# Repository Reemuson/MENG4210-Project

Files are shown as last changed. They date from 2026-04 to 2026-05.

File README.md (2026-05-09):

<p align="center" width="100%">
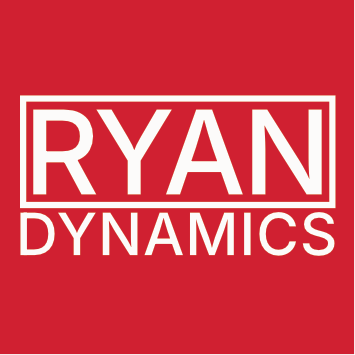
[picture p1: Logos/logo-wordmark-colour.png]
  
</p>

<h1 align="center">DREAM</h1>

<h2 align="center">Data Recording and Electrophysiological Acquisition Module</h2>

<p align="center" width="100%">
  <a href="https://github.com/Reemuson/MENG4210-Project/actions/workflows/ci.yaml">
    
  </a>
</p>

<p align="center" width="100%">
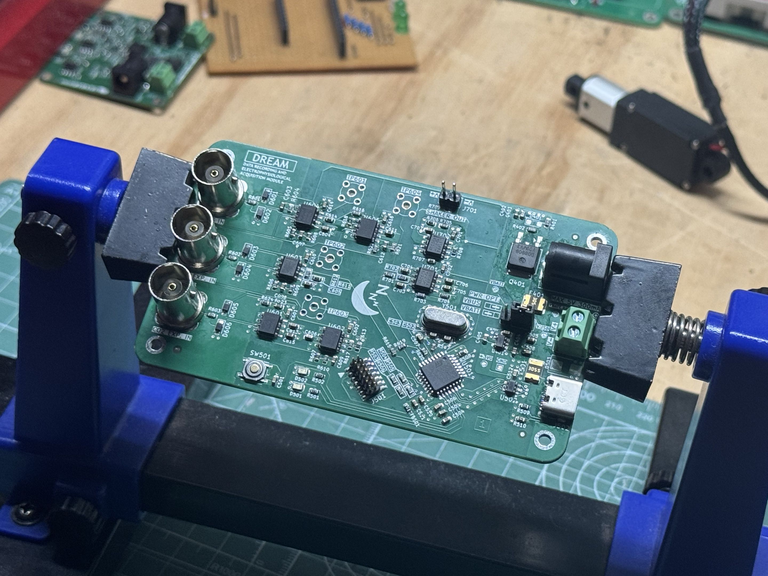
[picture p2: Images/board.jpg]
    
</p>

***

<p align="center">
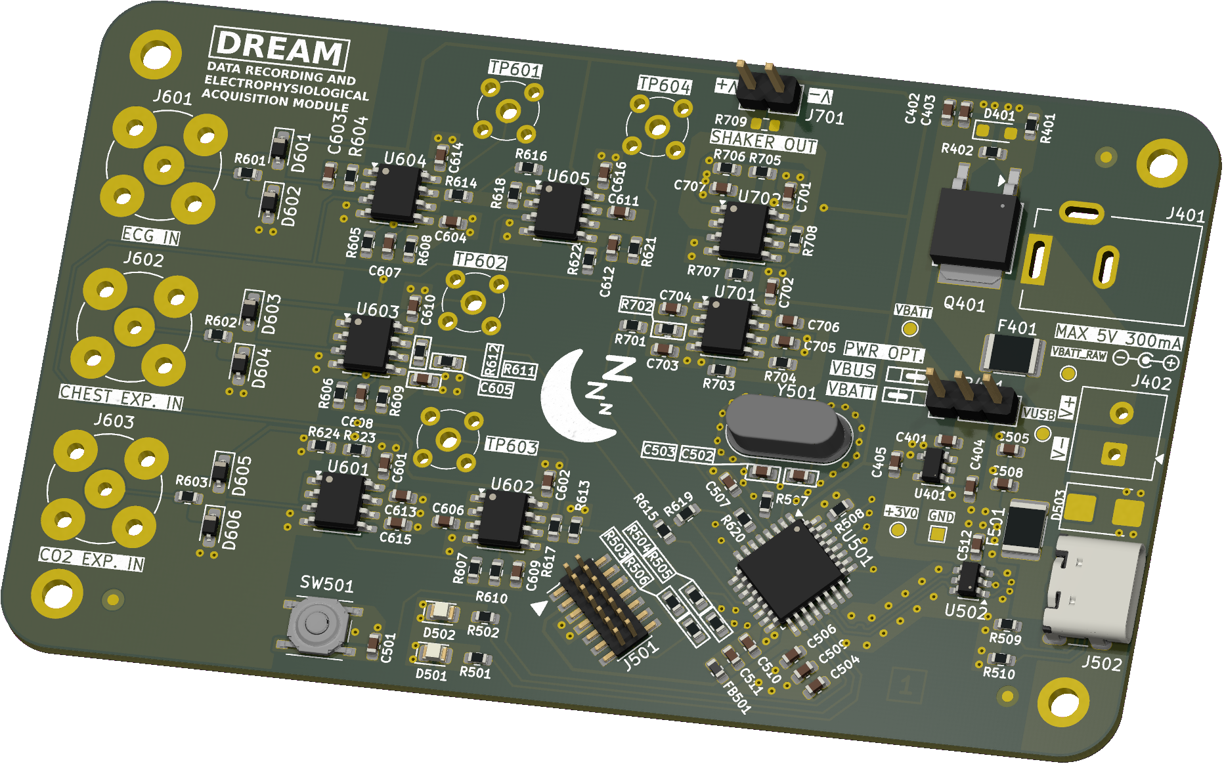
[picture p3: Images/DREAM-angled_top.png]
3D Top Angled
  
&nbsp; &nbsp; &nbsp; &nbsp;
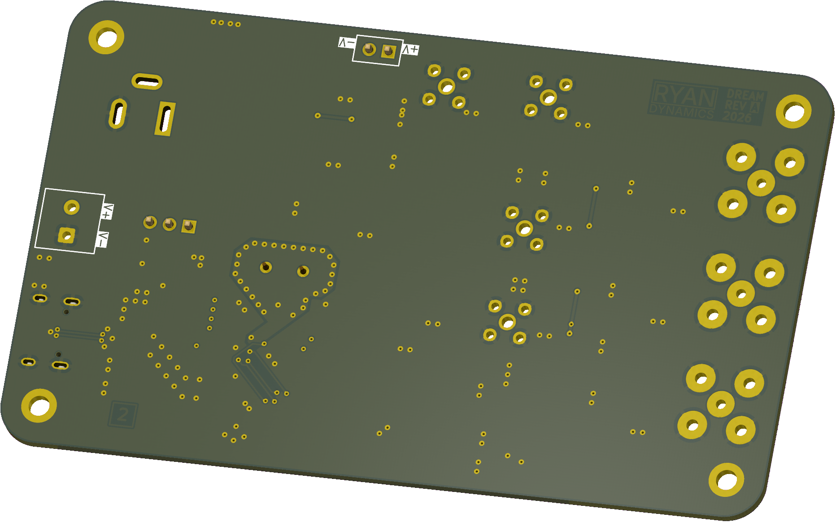
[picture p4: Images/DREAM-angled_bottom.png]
3D Bottom Angled
  
</p>

***

## SPECIFICATIONS

| Parameter | Value | 
| --- | --- |
| Dimensions | 100.0 × 60.0 mm |

***

## DIRECTORY STRUCTURE

    .
    ├─ Computations       # Misc calculations
    ├─ HTML               # HTML files for generated webpage
    ├─ Images             # Pictures and renders
    │
    ├─ kibot_resources    # External resources for KiBot
    │  ├─ colors          # Color theme for KiCad
    │  ├─ fonts           # Fonts used in the project
    │  ├─ scripts         # External scripts used with KiBot
    │  └─ templates       # Templates for KiBot generated reports
    │
    ├─ kibot_yaml         # KiBot YAML config files
    ├─ KiRI               # KiRI (PCB diff viewer) files
    │
    ├─ lib                # KiCad footprint and symbol libraries
    │  ├─ 3d_models       # Component 3D models
    │  ├─ lib_fp          # Footprint libraries
    │  └─ lib_sym         # Symbol libraries
    │
    ├─ Logos              # Logos
    │
    ├─ Manufacturing      # Assembly and fabrication documents
    │  ├─ Assembly        # Assembly documents (BoM, pos, notes)
    │  │
    │  └─ Fabrication     # Fabrication documents (ZIP, notes)
    │     ├─ Drill Tables # CSV drill tables
    │     └─ Gerbers      # Gerbers
    │
    ├─ Report             # Reports for ERC/DRC
    ├─ Schematic          # PDF of schematic
    ├─ Templates          # Title block templates
    ├─ Testing
    │  └─ Testpoints      # Testpoints tables      
    │
    └─ Variants           # Outputs for assembly variants

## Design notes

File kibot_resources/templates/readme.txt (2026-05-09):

<p align="center" width="100%">
  
</p>

<h1 align="center">${BOARD_NAME}</h1>

<h2 align="center">Data Recording and Electrophysiological Acquisition Module</h2>

<p align="center" width="100%">
  <a href="${GIT_URL}/actions/workflows/ci.yaml">
    CI Badge
  </a>
</p>

<p align="center" width="100%">
    
</p>

***

<p align="center">
  3D Top Angled
&nbsp; &nbsp; &nbsp; &nbsp;
  3D Bottom Angled
</p>

***

## SPECIFICATIONS

| Parameter | Value | 
| --- | --- |
| Dimensions | ${bb_w_mm} × ${bb_h_mm} mm |

***

## DIRECTORY STRUCTURE

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

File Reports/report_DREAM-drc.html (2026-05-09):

Logo

(https://github.com/INTI-CMNB/KiBot/) | DRC report for DREAM
| PCB: DREAM Revision: 1.2.0 Date: 2026-05-09T09:53:02+0000 KiCad Version: 9.0.7 | Errors: 2 Warnings: 344 Total: 346

Violations

Type | Description | Details
drill_out_of_range | Hole size out of range (rule 'MENG4210 Minimum Non-plated Hole Size' min hole 0.8000 mm; actual 0.6500 mm) | @(256.22 mm, 150.39 mm): NPTH pad of J502
drill_out_of_range | Hole size out of range (rule 'MENG4210 Minimum Non-plated Hole Size' min hole 0.8000 mm; actual 0.6500 mm) | @(256.22 mm, 144.61 mm): NPTH pad of J502
via_dangling | Via is not connected or connected on only one layer | @(237.43 mm, 143.45 mm): Via [unconnected-(U501-PB5-Pad28)] on L1 (Sig, PWR) - L2 (Sig, GND)
via_dangling | Via is not connected or connected on only one layer | @(237.43 mm, 142.18 mm): Via [unconnected-(U501-PB6-Pad29)] on L1 (Sig, PWR) - L2 (Sig, GND)
via_dangling | Via is not connected or connected on only one layer | @(237.43 mm, 140.91 mm): Via [unconnected-(U501-PB7-Pad30)] on L1 (Sig, PWR) - L2 (Sig, GND)
via_dangling | Via is not connected or connected on only one layer | @(238.7 mm, 147.26 mm): Via [unconnected-(U501-PA15-Pad25)] on L1 (Sig, PWR) - L2 (Sig, GND)
via_dangling | Via is not connected or connected on only one layer | @(237.43 mm, 144.72 mm): Via [unconnected-(U501-PB4-Pad27)] on L1 (Sig, PWR) - L2 (Sig, GND)
via_dangling | Via is not connected or connected on only one layer | @(224.879798 mm, 146.139798 mm): Via [unconnected-(U501-PA3-Pad8)] on L1 (Sig, PWR) - L2 (Sig, GND)
via_dangling | Via is not connected or connected on only one layer | @(224.095 mm, 144.72 mm): Via [unconnected-(U501-PA2-Pad7)] on L1 (Sig, PWR) - L2 (Sig, GND)
lib_footprint_mismatch | Footprint 'SOT-23-6' does not match copy in library 'Package_TO_SOT_SMD'. | @(247.5 mm, 147.5 mm): Footprint U502
lib_footprint_mismatch | Footprint 'R_0603_1608Metric' does not match copy in library 'Resistor_SMD'. | @(195.52 mm, 132.02 mm): Footprint R612
lib_footprint_mismatch | Footprint 'R_0603_1608Metric' does not match copy in library 'Resistor_SMD'. | @(192.98 mm, 122.685 mm): Footprint R608
lib_footprint_mismatch | Footprint 'D_SOD-323_HandSoldering' does not match copy in library 'Diode_SMD'. | @(180.0 mm, 150.0 mm): Footprint D606
lib_footprint_mismatch | Footprint 'R_0603_1608Metric' does not match copy in library 'Resistor_SMD'. | @(196.345 mm, 117.415 mm): Footprint R614
lib_footprint_mismatch | Footprint 'R_0603_1608Metric' does not match copy in library 'Resistor_SMD'. | @(208.855 mm, 122.05 mm): Footprint R622
lib_footprint_mismatch | Footprint 'R_0603_1608Metric' does not match copy in library 'Resistor_SMD'. | @(227.46 mm, 129.48 mm): Footprint R704
lib_footprint_mismatch | Footprint 'PinHeader_1x03_P2.54mm_Vertical' does not match copy in library 'Connector_PinHeader_2.54mm'. | @(242.46 mm, 131.5 mm): Footprint JP401
lib_footprint_mismatch | Footprint 'C_0603_1608Metric' does not match copy in library 'Capacitor_SMD'. | @(233.071992 mm, 156.063008 mm): Footprint C506
lib_footprint_mismatch | Footprint 'C_0603_1608Metric' does not match copy in library 'Capacitor_SMD'. | @(229.088008 mm, 155.428008 mm): Footprint C510
lib_footprint_mismatch | Footprint 'R_0603_1608Metric' does not match copy in library 'Resistor_SMD'. | @(198.06 mm, 132.655 mm): Footprint R611
lib_footprint_mismatch | Footprint 'R_0603_1608Metric' does not match copy in library 'Resistor_SMD'. | @(201.235 mm, 116.78 mm): Footprint R618
lib_footprint_mismatch | Footprint 'C_0603_1608Metric' does not match copy in library 'Capacitor_SMD'. | @(191.075 mm, 122.635 mm): Footprint C607
lib_footprint_mismatch | Footprint 'L_0603_1608Metric' does not match copy in library 'Inductor_SMD'. | @(226.635 mm, 158.055 mm): Footprint FB501
lib_footprint_mismatch | Footprint 'D_SOD-323_HandSoldering' does not match copy in library 'Diode_SMD'. | @(180.0 mm, 130.0 mm): Footprint D603
lib_footprint_mismatch | Footprint 'R_0603_1608Metric' does not match copy in library 'Resistor_SMD'. | @(221.4788 mm, 144.1612 mm): Footprint R619
lib_footprint_mismatch | Footprint 'D_SOD-323_HandSoldering' does not match copy in library 'Diode_SMD'. | @(180.0 mm, 135.0 mm): Footprint D604
lib_footprint_mismatch | Footprint 'R_0603_1608Metric' does not match copy in library 'Resistor_SMD'. | @(221.696698 mm, 152.356372 mm): Footprint R503
lib_footprint_mismatch | Footprint 'SOIC-8_3.9x4.9mm_P1.27mm' does not match copy in library 'Package_SO'. | @(191.075 mm, 146.625 mm): Footprint U601
lib_footprint_mismatch | Footprint 'C_0603_1608Metric' does not match copy in library 'Capacitor_SMD'. | @(196.155 mm, 159.185 mm): Footprint C501
lib_footprint_mismatch | Footprint 'R_0603_1608Metric' does not match copy in library 'Resistor_SMD'. | @(203.775 mm, 151.26 mm): Footprint R607
lib_footprint_mismatch | Footprint 'R_0603_1608Metric' does not match copy in library 'Resistor_SMD'. | @(210.125 mm, 146.625 mm): Footprint R617
lib_footprint_mismatch | Footprint 'R_0603_1608Metric' does not match copy in library 'Resistor_SMD'. | @(177.5 mm, 147.5 mm): Footprint R603
lib_footprint_mismatch | Footprint 'R_0603_1608Metric' does not match copy in library 'Resistor_SMD'. | @(186.63 mm, 116.78 mm): Footprint R604
lib_footprint_mismatch | Footprint 'R_0603_1608Metric' does not match copy in library 'Resistor_SMD'. | @(242.5 mm, 108.285499 mm): Footprint R402
lib_footprint_mismatch | Footprint 'C_0603_1608Metric' does not match copy in library 'Capacitor_SMD'. | @(224.816992 mm, 140.996992 mm): Footprint C507
lib_footprint_mismatch | Footprint 'D_SOD-323_HandSoldering' does not match copy in library 'Diode_SMD'. | @(180.0 mm, 145.0 mm): Footprint D605
lib_footprint_mismatch | Footprint 'R_1812_4532Metric' does not match copy in library 'Resistor_SMD'. | @(251.4 mm, 142.18 mm): Footprint F501
lib_footprint_mismatch | Footprint 'LQFP-32_7x7mm_P0.8mm' does not match copy in library 'Package_QFP'. | @(231.715 mm, 148.53 mm): Footprint U501
lib_footprint_mismatch | Footprint 'LED_0805_2012Metric' does not match copy in library 'LED_SMD'. | @(201.6668 mm, 159.325 mm): Footprint D501
lib_footprint_mismatch | Footprint 'R_0603_1608Metric' does not match copy in library 'Resistor_SMD'. | @(177.5 mm, 132.5 mm): Footprint R602
lib_footprint_mismatch | Footprint 'R_0603_1608Metric' does not match copy in library 'Resistor_SMD'. | @(226.635 mm, 118.05 mm): Footprint R708
lib_footprint_mismatch | Footprint 'PinHeader_1x02_P2.54mm_Vertical' does not match copy in library 'Connector_PinHeader_2.54mm'. | @(220.915 mm, 105.35 mm): Footprint J701
lib_footprint_mismatch | Footprint 'SOT-23-5' does not match copy in library 'Package_TO_SOT_SMD'. | @(242.5 mm, 137.5 mm): Footprint U401
lib_footprint_mismatch | Footprint 'R_0603_1608Metric' does not match copy in library 'Resistor_SMD'. | @(188.345 mm, 141.545 mm): Footprint R624
lib_footprint_mismatch | Footprint 'R_0603_1608Metric' does not match copy in library 'Resistor_SMD'. | @(191.52 mm, 141.545 mm): Footprint R623
lib_footprint_mismatch | Footprint 'C_0603_1608Metric' does not match copy in library 'Capacitor_SMD'. | @(184.725 mm, 116.78 mm): Footprint C603
lib_footprint_mismatch | Footprint 'R_0603_1608Metric' does not match copy in library 'Resistor_SMD'. | @(226.635 mm, 144.085 mm): Footprint R620
lib_footprint_mismatch | Footprint 'R_0603_1608Metric' does not match copy in library 'Resistor_SMD'. | @(219.775326 mm, 145.9138 mm): Footprint R615
lib_footprint_mismatch | Footprint 'SOIC-8_3.9x4.9mm_P1.27mm' does not match copy in library 'Package_SO'. | @(222.19 mm, 126.94 mm): Footprint U701
lib_footprint_mismatch | Footprint 'R_0603_1608Metric' does not match copy in library 'Resistor_SMD'. | @(245.5 mm, 105.460499 mm): Footprint R401
lib_footprint_mismatch | Footprint 'R_0603_1608Metric' does not match copy in library 'Resistor_SMD'. | @(222.19 mm, 130.75 mm): Footprint R703
lib_footprint_mismatch | Footprint 'C_0603_1608Metric' does not match copy in library 'Capacitor_SMD'. | @(194.25 mm, 142.675 mm): Footprint C601
lib_footprint_mismatch | Footprint 'R_0603_1608Metric' does not match copy in library 'Resistor_SMD'. | @(202.06 mm, 114.24 mm): Footprint R616
lib_footprint_mismatch | Footprint 'C_0603_1608Metric' does not match copy in library 'Capacitor_SMD'. | @(208.855 mm, 114.1 mm): Footprint C616
lib_footprint_mismatch | Footprint 'R_0603_1608Metric' does not match copy in library 'Resistor_SMD'. | @(189.17 mm, 136.655 mm): Footprint R606
lib_footprint_mismatch | Footprint 'R_0603_1608Metric' does not match copy in library 'Resistor_SMD'. | @(205.68 mm, 151.26 mm): Footprint R610
lib_footprint_mismatch | Footprint 'R_0603_1608Metric' does not match copy in library 'Resistor_SMD'. | @(251.4 mm, 154.245 mm): Footprint R510
lib_footprint_mismatch | Footprint 'R_0603_1608Metric' does not match copy in library 'Resistor_SMD'. | @(177.5 mm, 117.5 mm): Footprint R601
lib_footprint_mismatch | Footprint 'C_0603_1608Metric' does not match copy in library 'Capacitor_SMD'. | @(196.295 mm, 145.355 mm): Footprint C613
lib_footprint_mismatch | Footprint 'C_0603_1608Metric' does not match copy in library 'Capacitor_SMD'. | @(235.611992 mm, 158.603008 mm): Footprint C504
lib_footprint_mismatch | Footprint 'D_SOD-323_HandSoldering' does not match copy in library 'Diode_SMD'. | @(180.0 mm, 115.0 mm): Footprint D601
lib_footprint_mismatch | Footprint 'R_0603_1608Metric' does not match copy in library 'Resistor_SMD'. | @(211.9284 mm, 146.625 mm): Footprint R613
lib_footprint_mismatch | Footprint 'C_0603_1608Metric' does not match copy in library 'Capacitor_SMD'. | @(200.46 mm, 147.26 mm): Footprint C606
lib_footprint_mismatch | Footprint 'D_SOD-323_HandSoldering' does not match copy in library 'Diode_SMD'. | @(180.0 mm, 120.0 mm): Footprint D602
lib_footprint_mismatch | Footprint 'SOIC-8_3.9x4.9mm_P1.27mm' does not match copy in library 'Package_SO'. | @(205.68 mm, 146.625 mm): Footprint U602
lib_footprint_mismatch | Footprint 'C_0603_1608Metric' does not match copy in library 'Capacitor_SMD'. | @(239.0 mm, 137.499999 mm): Footprint C405
lib_footprint_mismatch | Footprint 'C_0603_1608Metric' does not match copy in library 'Capacitor_SMD'. | @(227.41 mm, 127.575 mm): Footprint C705
lib_footprint_mismatch | Footprint 'LED_0805_2012Metric' does not match copy in library 'LED_SMD'. | @(201.6668 mm, 155.515 mm): Footprint D502
lib_footprint_mismatch | Footprint 'C_0603_1608Metric' does not match copy in library 'Capacitor_SMD'. | @(234.341992 mm, 157.333008 mm): Footprint C509
lib_footprint_mismatch | Footprint 'R_0603_1608Metric' does not match copy in library 'Resistor_SMD'. | @(213.745 mm, 127.575 mm): Footprint R701
lib_footprint_mismatch | Footprint 'R_0603_1608Metric' does not match copy in library 'Resistor_SMD'. | @(205.4768 mm, 159.325 mm): Footprint R501
lib_footprint_mismatch | Footprint 'C_0603_1608Metric' does not match copy in library 'Capacitor_SMD'. | @(227.41 mm, 125.67 mm): Footprint C706
lib_footprint_mismatch | Footprint 'C_0603_1608Metric' does not match copy in library 'Capacitor_SMD'. | @(194.25 mm, 128.07 mm): Footprint C610
lib_footprint_mismatch | Footprint 'C_0603_1608Metric' does not match copy in library 'Capacitor_SMD'. | @(191.075 mm, 136.605 mm): Footprint C608
lib_footprint_mismatch | Footprint 'R_0603_1608Metric' does not match copy in library 'Resistor_SMD'. | @(234.838363 mm, 142.231637 mm): Footprint R508
lib_footprint_mismatch | Footprint 'C_0603_1608Metric' does not match copy in library 'Capacitor_SMD'. | @(248.86 mm, 135.195 mm): Footprint C505
lib_footprint_mismatch | Footprint 'R_0603_1608Metric' does not match copy in library 'Resistor_SMD'. | @(228.286 mm, 142.434 mm): Footprint R507
lib_footprint_mismatch | Footprint 'R_1812_4532Metric' does not match copy in library 'Resistor_SMD'. | @(247.5 mm, 126.5 mm): Footprint F401
lib_footprint_mismatch | Footprint 'TerminalBlock_Phoenix_MKDS-1-2-3.81_1x02_P3.81mm_Horizontal' does not match copy in library 'TerminalBlock_Phoenix'. | @(257.972301 mm, 134.433001 mm): Footprint J402
lib_footprint_mismatch | Footprint 'BarrelJack_Kycon_KLDX-0202-xC_Horizontal' does not match copy in library 'Connector_BarrelJack'. | @(248.05 mm, 117.5 mm): Footprint J401
lib_footprint_mismatch | Footprint 'SOIC-8_3.9x4.9mm_P1.27mm' does not match copy in library 'Package_SO'. | @(191.075 mm, 118.05 mm): Footprint U604
lib_footprint_mismatch | Footprint 'R_0603_1608Metric' does not match copy in library 'Resistor_SMD'. | @(216.92 mm, 127.575 mm): Footprint R702
lib_footprint_mismatch | Footprint 'SOIC-8_3.9x4.9mm_P1.27mm' does not match copy in library 'Package_SO'. | @(191.075 mm, 132.02 mm): Footprint U603
lib_footprint_mismatch | Footprint 'C_0603_1608Metric' does not match copy in library 'Capacitor_SMD'. | @(219.46 mm, 114.24 mm): Footprint C707
lib_footprint_mismatch | Footprint 'R_0603_1608Metric' does not match copy in library 'Resistor_SMD'. | @(223.941762 mm, 154.601438 mm): Footprint R506
lib_footprint_mismatch | Footprint 'R_0603_1608Metric' does not match copy in library 'Resistor_SMD'. | @(251.4 mm, 151.07 mm): Footprint R509
lib_footprint_mismatch | Footprint 'C_0603_1608Metric' does not match copy in library 'Capacitor_SMD'. | @(243.275 mm, 135.0 mm): Footprint C401
lib_footprint_mismatch | Footprint 'C_0603_1608Metric' does not match copy in library 'Capacitor_SMD'. | @(248.86 mm, 138.37 mm): Footprint C508
lib_footprint_mismatch | Footprint 'R_0603_1608Metric' does not match copy in library 'Resistor_SMD'. | @(212.665 mm, 120.59 mm): Footprint R621
lib_footprint_mismatch | Footprint 'C_0603_1608Metric' does not match copy in library 'Capacitor_SMD'. | @(194.25 mm, 114.1 mm): Footprint C614
lib_footprint_mismatch | Footprint 'R_0603_1608Metric' does not match copy in library 'Resistor_SMD'. | @(225.872163 mm, 153.837763 mm): Footprint R505
lib_footprint_mismatch | Footprint 'C_0603_1608Metric' does not match copy in library 'Capacitor_SMD'. | @(216.92 mm, 129.48 mm): Footprint C703
lib_footprint_mismatch | Footprint 'C_0603_1608Metric' does not match copy in library 'Capacitor_SMD'. | @(225.365 mm, 122.99 mm): Footprint C702
lib_footprint_mismatch | Footprint 'C_0603_1608Metric' does not match copy in library 'Capacitor_SMD'. | @(196.295 mm, 134.56 mm): Footprint C605
lib_footprint_mismatch | Footprint 'C_0603_1608Metric' does not match copy in library 'Capacitor_SMD'. | @(238.0 mm, 105.0 mm): Footprint C402
lib_footprint_mismatch | Footprint 'C_0603_1608Metric' does not match copy in library 'Capacitor_SMD'. | @(210.76 mm, 120.59 mm): Footprint C612
lib_footprint_mismatch | Footprint 'C_0603_1608Metric' does not match copy in library 'Capacitor_SMD'. | @(247.5 mm, 144.225 mm): Footprint C512
lib_footprint_mismatch | Footprint 'C_0603_1608Metric' does not match copy in library 'Capacitor_SMD'. | @(225.365 mm, 114.1 mm): Footprint C701
lib_footprint_mismatch | Footprint 'R_0603_1608Metric' does not match copy in library 'Resistor_SMD'. | @(222.0884 mm, 107.89 mm): Footprint R709
lib_footprint_mismatch | Footprint 'C_0603_1608Metric' does not match copy in library 'Capacitor_SMD'. | @(196.295 mm, 119.955 mm): Footprint C604
lib_footprint_mismatch | Footprint 'C_0603_1608Metric' does not match copy in library 'Capacitor_SMD'. | @(230.840001 mm, 139.64 mm): Footprint C502
lib_footprint_mismatch | Footprint 'SOIC-8_3.9x4.9mm_P1.27mm' does not match copy in library 'Package_SO'. | @(222.19 mm, 118.05 mm): Footprint U702
lib_footprint_mismatch | Footprint 'C_0603_1608Metric' does not match copy in library 'Capacitor_SMD'. | @(207.585 mm, 151.21 mm): Footprint C609
lib_footprint_mismatch | Footprint 'R_0603_1608Metric' does not match copy in library 'Resistor_SMD'. | @(219.46 mm, 112.335 mm): Footprint R706
lib_footprint_mismatch | Footprint 'C_0603_1608Metric' does not match copy in library 'Capacitor_SMD'. | @(246.0 mm, 139.025 mm): Footprint C404
lib_footprint_mismatch | Footprint 'R_0603_1608Metric' does not match copy in library 'Resistor_SMD'. | @(205.4768 mm, 155.515 mm): Footprint R502
lib_footprint_mismatch | Footprint 'C_0603_1608Metric' does not match copy in library 'Capacitor_SMD'. | @(216.97 mm, 125.67 mm): Footprint C704
lib_footprint_mismatch | Footprint 'SOIC-8_3.9x4.9mm_P1.27mm' does not match copy in library 'Package_SO'. | @(205.68 mm, 118.05 mm): Footprint U605
lib_footprint_mismatch | Footprint 'C_0603_1608Metric' does not match copy in library 'Capacitor_SMD'. | @(239.5 mm, 105.0 mm): Footprint C403
lib_footprint_mismatch | Footprint 'R_0603_1608Metric' does not match copy in library 'Resistor_SMD'. | @(192.98 mm, 136.655 mm): Footprint R609
lib_footprint_mismatch | Footprint 'PinHeader_2x07_P1.27mm_Vertical_SMD' does not match copy in library 'Connector_PinHeader_1.27mm'. | @(215.84 mm, 153.61 mm): Footprint J501
lib_footprint_mismatch | Footprint 'C_0603_1608Metric' does not match copy in library 'Capacitor_SMD'. | @(227.818008 mm, 156.698008 mm): Footprint C511
lib_footprint_mismatch | Footprint 'R_0603_1608Metric' does not match copy in library 'Resistor_SMD'. | @(189.17 mm, 122.685 mm): Footprint R605
lib_footprint_mismatch | Footprint 'C_0603_1608Metric' does not match copy in library 'Capacitor_SMD'. | @(210.9 mm, 117.415 mm): Footprint C611
lib_footprint_mismatch | Footprint 'R_0603_1608Metric' does not match copy in library 'Resistor_SMD'. | @(222.635 mm, 112.335 mm): Footprint R705
lib_footprint_mismatch | Footprint 'C_0603_1608Metric' does not match copy in library 'Capacitor_SMD'. | @(208.855 mm, 142.675 mm): Footprint C602
lib_footprint_mismatch | Footprint 'C_0603_1608Metric' does not match copy in library 'Capacitor_SMD'. | @(227.511 mm, 139.64 mm): Footprint C503
lib_footprint_mismatch | Footprint 'R_0603_1608Metric' does not match copy in library 'Resistor_SMD'. | @(223.627099 mm, 151.592697 mm): Footprint R504
lib_footprint_mismatch | Footprint 'R_0603_1608Metric' does not match copy in library 'Resistor_SMD'. | @(222.19 mm, 121.86 mm): Footprint R707
lib_footprint_mismatch | Footprint 'C_0603_1608Metric' does not match copy in library 'Capacitor_SMD'. | @(196.295 mm, 147.895 mm): Footprint C615
silk_over_copper | Silkscreen clipped by solder mask | @(194.8088 mm, 133.8488 mm): Rectangle on F.Silkscreen
silk_over_copper | Silkscreen clipped by solder mask | @(226.0 mm, 138.9288 mm): Rectangle on F.Silkscreen
silk_over_copper | Silkscreen clipped by solder mask | @(229.4036 mm, 138.9288 mm): Rectangle on F.Silkscreen
silk_over_copper | Silkscreen clipped by solder mask | @(247.5 mm, 150.25 mm): Reference field of U502
silk_over_copper | Silkscreen clipped by solder mask | @(231.1816 mm, 157.4708 mm): Reference field of C510
silk_over_copper | Silkscreen clipped by solder mask | @(191.075 mm, 125.035 mm): Reference field of C607
silk_over_copper | Silkscreen clipped by solder mask | @(248.75 mm, 142.18 mm): Reference field of F501
silk_over_copper | Silkscreen clipped by solder mask | @(236.9728 mm, 145.532801 mm): Reference field of U501
silk_over_copper | Silkscreen clipped by solder mask | @(199.9818 mm, 158.365 mm): Segment of D501 on F.Silkscreen
silk_over_copper | Silkscreen clipped by solder mask | @(199.9818 mm, 160.285 mm): Segment of D501 on F.Silkscreen
silk_over_copper | Silkscreen clipped by solder mask | @(202.6668 mm, 158.365 mm): Segment of D501 on F.Silkscreen
silk_over_copper | Silkscreen clipped by solder mask | @(191.52 mm, 140.275 mm): Reference field of R623
silk_over_copper | Silkscreen clipped by solder mask | @(254.335001 mm, 137.49 mm): Segment of D503 on F.Silkscreen
silk_over_copper | Silkscreen clipped by solder mask | @(254.335001 mm, 141.79 mm): Segment of D503 on F.Silkscreen
silk_over_copper | Silkscreen clipped by solder mask | @(212.03 mm, 143.45 mm): Reference field of R613
silk_over_copper | Silkscreen clipped by solder mask | @(230.445 mm, 127.575 mm): Reference field of C705
silk_over_copper | Silkscreen clipped by solder mask | @(199.9818 mm, 154.555 mm): Segment of D502 on F.Silkscreen
silk_over_copper | Silkscreen clipped by solder mask | @(199.9818 mm, 156.475 mm): Segment of D502 on F.Silkscreen
silk_over_copper | Silkscreen clipped by solder mask | @(202.6668 mm, 154.555 mm): Segment of D502 on F.Silkscreen
silk_over_copper | Silkscreen clipped by solder mask | @(236.5156 mm, 155.184801 mm): Reference field of C509
silk_over_copper | Silkscreen clipped by solder mask | @(191.075 mm, 139.005 mm): Reference field of C608
silk_over_copper | Silkscreen clipped by solder mask | @(248.86 mm, 133.925 mm): Reference field of C505
silk_over_copper | Silkscreen clipped by solder mask | @(230.445 mm, 141.799 mm): Reference field of R507
silk_over_copper | Silkscreen clipped by solder mask | @(193.135 mm, 120.61 mm): Segment of U604 on F.Silkscreen
silk_over_copper | Silkscreen clipped by solder mask | @(193.135 mm, 134.58 mm): Segment of U603 on F.Silkscreen
silk_over_copper | Silkscreen clipped by solder mask | @(216.475 mm, 114.24 mm): Reference field of C707
silk_over_copper | Silkscreen clipped by solder mask | @(239.97 mm, 135.0 mm): Reference field of C401
silk_over_copper | Silkscreen clipped by solder mask | @(248.86 mm, 137.1 mm): Reference field of C508
silk_over_copper | Silkscreen clipped by solder mask | @(222.7488 mm, 114.6464 mm): Reference field of U702
silk_over_copper | Silkscreen clipped by solder mask | @(229.81 mm, 158.69 mm): Reference field of C511
nonmirrored_text_on_back_layer | Non-Mirrored text on back layer | @(225.238 mm, 104.7404 mm): PCB text 'V-' on B.Silkscreen
nonmirrored_text_on_back_layer | Non-Mirrored text on back layer | @(219.2436 mm, 104.7404 mm): PCB text 'V+' on B.Silkscreen

Schematic parity

Type | Description | Details
net_conflict | Pad net (/ARCHITECTURE/DIGITAL AND HMI/BTN) doesn't match net given by schematic (/CIRCUIT/BTN). | @(196.155 mm, 159.96 mm): Pad 2 [/ARCHITECTURE/DIGITAL AND HMI/BTN] of C501 on L1 (Sig, PWR)
net_conflict | Pad net (/ARCHITECTURE/DIGITAL AND HMI/OSC_IN) doesn't match net given by schematic (/CIRCUIT/OSC_IN). | @(231.615001 mm, 139.64 mm): Pad 2 [/ARCHITECTURE/DIGITAL AND HMI/OSC_IN] of C502 on L1 (Sig, PWR)
net_conflict | Pad net (/ARCHITECTURE/DIGITAL AND HMI/XTAL) doesn't match net given by schematic (/CIRCUIT/XTAL). | @(226.736 mm, 139.64 mm): Pad 1 [/ARCHITECTURE/DIGITAL AND HMI/XTAL] of C503 on L1 (Sig, PWR)
net_conflict | Pad net (/ARCHITECTURE/DIGITAL AND HMI/~{RST}) doesn't match net given by schematic (/CIRCUIT/~{RST}). | @(225.365 mm, 141.545 mm): Pad 2 [/ARCHITECTURE/DIGITAL AND HMI/~{RST}] of C507 on L1 (Sig, PWR)
net_conflict | Pad net (/ARCHITECTURE/DIGITAL AND HMI/VDDA) doesn't match net given by schematic (VDDA). | @(228.54 mm, 154.88 mm): Pad 2 [/ARCHITECTURE/DIGITAL AND HMI/VDDA] of C510 on L1 (Sig, PWR)
net_conflict | Pad net (/ARCHITECTURE/DIGITAL AND HMI/VDDA) doesn't match net given by schematic (VDDA). | @(227.27 mm, 156.15 mm): Pad 2 [/ARCHITECTURE/DIGITAL AND HMI/VDDA] of C511 on L1 (Sig, PWR)
net_conflict | Pad net (/ARCHITECTURE/ANALOGUE INPUTS/ECG_LPF1) doesn't match net given by schematic (/CIRCUIT/ECG_LPF1). | @(184.725 mm, 116.005 mm): Pad 1 [/ARCHITECTURE/ANALOGUE INPUTS/ECG_LPF1] of C603 on L1 (Sig, PWR)
net_conflict | Pad net (/ARCHITECTURE/ANALOGUE INPUTS/ECG_LPF1_N) doesn't match net given by schematic (/CIRCUIT/ECG_LPF1_N). | @(184.725 mm, 117.555 mm): Pad 2 [/ARCHITECTURE/ANALOGUE INPUTS/ECG_LPF1_N] of C603 on L1 (Sig, PWR)
net_conflict | Pad net (/ARCHITECTURE/ANALOGUE INPUTS/ECG_SK_RC) doesn't match net given by schematic (/CIRCUIT/ECG_SK_RC). | @(195.52 mm, 119.955 mm): Pad 1 [/ARCHITECTURE/ANALOGUE INPUTS/ECG_SK_RC] of C604 on L1 (Sig, PWR)
net_conflict | Pad net (/ARCHITECTURE/ANALOGUE INPUTS/CE_SK_RC) doesn't match net given by schematic (/CIRCUIT/CE_SK_RC). | @(195.52 mm, 134.56 mm): Pad 1 [/ARCHITECTURE/ANALOGUE INPUTS/CE_SK_RC] of C605 on L1 (Sig, PWR)
net_conflict | Pad net (/ARCHITECTURE/ANALOGUE INPUTS/CO2_SK_RC) doesn't match net given by schematic (/CIRCUIT/CO2_SK_RC). | @(201.235 mm, 147.26 mm): Pad 1 [/ARCHITECTURE/ANALOGUE INPUTS/CO2_SK_RC] of C606 on L1 (Sig, PWR)
net_conflict | Pad net (/ARCHITECTURE/ANALOGUE INPUTS/ECG_FILT) doesn't match net given by schematic (/CIRCUIT/ECG_FILT). | @(191.075 mm, 121.86 mm): Pad 1 [/ARCHITECTURE/ANALOGUE INPUTS/ECG_FILT] of C607 on L1 (Sig, PWR)
net_conflict | Pad net (/ARCHITECTURE/ANALOGUE INPUTS/ECG_SK_MID) doesn't match net given by schematic (/CIRCUIT/ECG_SK_MID). | @(191.075 mm, 123.41 mm): Pad 2 [/ARCHITECTURE/ANALOGUE INPUTS/ECG_SK_MID] of C607 on L1 (Sig, PWR)
net_conflict | Pad net (/ARCHITECTURE/ANALOGUE INPUTS/CE_FILT) doesn't match net given by schematic (/CIRCUIT/CE_FILT). | @(191.075 mm, 135.83 mm): Pad 1 [/ARCHITECTURE/ANALOGUE INPUTS/CE_FILT] of C608 on L1 (Sig, PWR)
net_conflict | Pad net (/ARCHITECTURE/ANALOGUE INPUTS/CE_SK_MID) doesn't match net given by schematic (/CIRCUIT/CE_SK_MID). | @(191.075 mm, 137.38 mm): Pad 2 [/ARCHITECTURE/ANALOGUE INPUTS/CE_SK_MID] of C608 on L1 (Sig, PWR)
net_conflict | Pad net (/ARCHITECTURE/ANALOGUE INPUTS/CO2_FILT) doesn't match net given by schematic (/CIRCUIT/CO2_FILT). | @(207.585 mm, 150.435 mm): Pad 1 [/ARCHITECTURE/ANALOGUE INPUTS/CO2_FILT] of C609 on L1 (Sig, PWR)
net_conflict | Pad net (/ARCHITECTURE/ANALOGUE INPUTS/CO2_SK_MID) doesn't match net given by schematic (/CIRCUIT/CO2_SK_MID). | @(207.585 mm, 151.985 mm): Pad 2 [/ARCHITECTURE/ANALOGUE INPUTS/CO2_SK_MID] of C609 on L1 (Sig, PWR)
net_conflict | Pad net (/ARCHITECTURE/ANALOGUE INPUTS/SERVO_N) doesn't match net given by schematic (/CIRCUIT/SERVO_N). | @(211.675 mm, 117.415 mm): Pad 1 [/ARCHITECTURE/ANALOGUE INPUTS/SERVO_N] of C611 on L1 (Sig, PWR)
net_conflict | Pad net (/ARCHITECTURE/ANALOGUE INPUTS/SERVO_OUT) doesn't match net given by schematic (/CIRCUIT/SERVO_OUT). | @(210.125 mm, 117.415 mm): Pad 2 [/ARCHITECTURE/ANALOGUE INPUTS/SERVO_OUT] of C611 on L1 (Sig, PWR)
net_conflict | Pad net (/ARCHITECTURE/ANALOGUE INPUTS/SERVO_P) doesn't match net given by schematic (/CIRCUIT/SERVO_P). | @(210.76 mm, 119.815 mm): Pad 2 [/ARCHITECTURE/ANALOGUE INPUTS/SERVO_P] of C612 on L1 (Sig, PWR)
net_conflict | Pad net (/ARCHITECTURE/ANALOGUE OUTPUTS/SHK_SK1_RC) doesn't match net given by schematic (/CIRCUIT/SHK_SK1_RC). | @(216.145 mm, 129.48 mm): Pad 1 [/ARCHITECTURE/ANALOGUE OUTPUTS/SHK_SK1_RC] of C703 on L1 (Sig, PWR)
net_conflict | Pad net (/ARCHITECTURE/ANALOGUE OUTPUTS/SHK_FILT1) doesn't match net given by schematic (/CIRCUIT/SHK_FILT1). | @(217.745 mm, 125.67 mm): Pad 1 [/ARCHITECTURE/ANALOGUE OUTPUTS/SHK_FILT1] of C704 on L1 (Sig, PWR)
net_conflict | Pad net (/ARCHITECTURE/ANALOGUE OUTPUTS/SHK_SK1_MID) doesn't match net given by schematic (/CIRCUIT/SHK_SK1_MID). | @(216.195 mm, 125.67 mm): Pad 2 [/ARCHITECTURE/ANALOGUE OUTPUTS/SHK_SK1_MID] of C704 on L1 (Sig, PWR)
net_conflict | Pad net (/ARCHITECTURE/ANALOGUE OUTPUTS/SHK_SK2_RC) doesn't match net given by schematic (/CIRCUIT/SHK_SK2_RC). | @(226.635 mm, 127.575 mm): Pad 1 [/ARCHITECTURE/ANALOGUE OUTPUTS/SHK_SK2_RC] of C705 on L1 (Sig, PWR)
net_conflict | Pad net (/ARCHITECTURE/ANALOGUE OUTPUTS/SHK_FILT2) doesn't match net given by schematic (/CIRCUIT/SHK_FILT2). | @(226.635 mm, 125.67 mm): Pad 1 [/ARCHITECTURE/ANALOGUE OUTPUTS/SHK_FILT2] of C706 on L1 (Sig, PWR)
net_conflict | Pad net (/ARCHITECTURE/ANALOGUE OUTPUTS/SHK_SK2_MID) doesn't match net given by schematic (/CIRCUIT/SHK_SK2_MID). | @(228.185 mm, 125.67 mm): Pad 2 [/ARCHITECTURE/ANALOGUE OUTPUTS/SHK_SK2_MID] of C706 on L1 (Sig, PWR)
net_conflict | Pad net (/ARCHITECTURE/ANALOGUE OUTPUTS/VREF_SHK) doesn't match net given by schematic (/CIRCUIT/VREF_SHK). | @(220.235 mm, 114.24 mm): Pad 1 [/ARCHITECTURE/ANALOGUE OUTPUTS/VREF_SHK] of C707 on L1 (Sig, PWR)
net_conflict | Pad net (/ARCHITECTURE/POWER/GATE_RPP) doesn't match net given by schematic (/CIRCUIT/GATE_RPP). | @(243.75 mm, 106.285499 mm): Pad 2 [/ARCHITECTURE/POWER/GATE_RPP] of D401 on L1 (Sig, PWR)
net_conflict | Pad net (/ARCHITECTURE/ANALOGUE INPUTS/ECG_LPF1_N) doesn't match net given by schematic (/CIRCUIT/ECG_LPF1_N). | @(180.0 mm, 116.249999 mm): Pad 2 [/ARCHITECTURE/ANALOGUE INPUTS/ECG_LPF1_N] of D601 on L1 (Sig, PWR)
net_conflict | Pad net (/ARCHITECTURE/ANALOGUE INPUTS/ECG_LPF1_N) doesn't match net given by schematic (/CIRCUIT/ECG_LPF1_N). | @(180.0 mm, 118.750001 mm): Pad 1 [/ARCHITECTURE/ANALOGUE INPUTS/ECG_LPF1_N] of D602 on L1 (Sig, PWR)
net_conflict | Pad net (/ARCHITECTURE/ANALOGUE INPUTS/CE_BUFF_IN) doesn't match net given by schematic (/CIRCUIT/CE_BUFF_IN). | @(180.0 mm, 131.249999 mm): Pad 2 [/ARCHITECTURE/ANALOGUE INPUTS/CE_BUFF_IN] of D603 on L1 (Sig, PWR)
net_conflict | Pad net (/ARCHITECTURE/ANALOGUE INPUTS/CE_BUFF_IN) doesn't match net given by schematic (/CIRCUIT/CE_BUFF_IN). | @(180.0 mm, 133.750001 mm): Pad 1 [/ARCHITECTURE/ANALOGUE INPUTS/CE_BUFF_IN] of D604 on L1 (Sig, PWR)
net_conflict | Pad net (/ARCHITECTURE/ANALOGUE INPUTS/CO2_BUFF_IN) doesn't match net given by schematic (/CIRCUIT/CO2_BUFF_IN). | @(180.0 mm, 146.249999 mm): Pad 2 [/ARCHITECTURE/ANALOGUE INPUTS/CO2_BUFF_IN] of D605 on L1 (Sig, PWR)
net_conflict | Pad net (/ARCHITECTURE/ANALOGUE INPUTS/CO2_BUFF_IN) doesn't match net given by schematic (/CIRCUIT/CO2_BUFF_IN). | @(180.0 mm, 148.750001 mm): Pad 1 [/ARCHITECTURE/ANALOGUE INPUTS/CO2_BUFF_IN] of D606 on L1 (Sig, PWR)
net_conflict | Pad net (/ARCHITECTURE/POWER/VBATT_RAW) doesn't match net given by schematic (/CIRCUIT/VBATT_RAW). | @(249.6375 mm, 126.5 mm): Pad 1 [/ARCHITECTURE/POWER/VBATT_RAW] of F401 on L1 (Sig, PWR)
net_conflict | Pad net (/ARCHITECTURE/POWER/VBATT_FUSED) doesn't match net given by schematic (/CIRCUIT/VBATT_FUSED). | @(245.3625 mm, 126.5 mm): Pad 2 [/ARCHITECTURE/POWER/VBATT_FUSED] of F401 on L1 (Sig, PWR)
net_conflict | Pad net (/ARCHITECTURE/DIGITAL AND HMI/VBUS) doesn't match net given by schematic (/CIRCUIT/VBUS). | @(251.4 mm, 144.3175 mm): Pad 1 [/ARCHITECTURE/DIGITAL AND HMI/VBUS] of F501 on L1 (Sig, PWR)
net_conflict | Pad net (/ARCHITECTURE/DIGITAL AND HMI/VDDA) doesn't match net given by schematic (VDDA). | @(226.078153 mm, 157.498153 mm): Pad 1 [/ARCHITECTURE/DIGITAL AND HMI/VDDA] of FB501 on L1 (Sig, PWR)
net_conflict | Pad net (/ARCHITECTURE/POWER/VBATT_RAW) doesn't match net given by schematic (/CIRCUIT/VBATT_RAW). | @(248.05 mm, 117.5 mm): PTH pad 1 [/ARCHITECTURE/POWER/VBATT_RAW] of J401
net_conflict | Pad net (/ARCHITECTURE/POWER/VBATT_RAW) doesn't match net given by schematic (/CIRCUIT/VBATT_RAW). | @(257.972301 mm, 130.623001 mm): PTH pad 2 [/ARCHITECTURE/POWER/VBATT_RAW] of J402
footprint_symbol_mismatch | Value (J501) doesn't match symbol value (Conn_ST_STDC14). | @(215.84 mm, 153.61 mm): Footprint J501
net_conflict | Pad net (/ARCHITECTURE/DIGITAL AND HMI/VBUS) doesn't match net given by schematic (/CIRCUIT/VBUS). | @(255.145 mm, 149.9 mm): Pad A4 [/ARCHITECTURE/DIGITAL AND HMI/VBUS] of J502 on L1 (Sig, PWR)
net_conflict | Pad net (/ARCHITECTURE/DIGITAL AND HMI/CC1) doesn't match net given by schematic (/CIRCUIT/CC1). | @(255.145001 mm, 148.75 mm): Pad A5 [/ARCHITECTURE/DIGITAL AND HMI/CC1] of J502 on L1 (Sig, PWR)
net_conflict | Pad net (/ARCHITECTURE/DIGITAL AND HMI/D+) doesn't match net given by schematic (/CIRCUIT/D+). | @(255.145 mm, 147.75 mm): Pad A6 [/ARCHITECTURE/DIGITAL AND HMI/D+] of J502 on L1 (Sig, PWR)
net_conflict | Pad net (/ARCHITECTURE/DIGITAL AND HMI/D-) doesn't match net given by schematic (/CIRCUIT/D-). | @(255.145 mm, 147.25 mm): Pad A7 [/ARCHITECTURE/DIGITAL AND HMI/D-] of J502 on L1 (Sig, PWR)
net_conflict | Pad net (/ARCHITECTURE/DIGITAL AND HMI/VBUS) doesn't match net given by schematic (/CIRCUIT/VBUS). | @(255.145 mm, 145.1 mm): Pad A9 [/ARCHITECTURE/DIGITAL AND HMI/VBUS] of J502 on L1 (Sig, PWR)
net_conflict | Pad net (/ARCHITECTURE/DIGITAL AND HMI/VBUS) doesn't match net given by schematic (/CIRCUIT/VBUS). | @(255.145 mm, 145.1 mm): Pad B4 [/ARCHITECTURE/DIGITAL AND HMI/VBUS] of J502 on L1 (Sig, PWR)
net_conflict | Pad net (/ARCHITECTURE/DIGITAL AND HMI/CC2) doesn't match net given by schematic (/CIRCUIT/CC2). | @(255.145 mm, 145.75 mm): Pad B5 [/ARCHITECTURE/DIGITAL AND HMI/CC2] of J502 on L1 (Sig, PWR)
net_conflict | Pad net (/ARCHITECTURE/DIGITAL AND HMI/D+) doesn't match net given by schematic (/CIRCUIT/D+). | @(255.145 mm, 146.75 mm): Pad B6 [/ARCHITECTURE/DIGITAL AND HMI/D+] of J502 on L1 (Sig, PWR)
net_conflict | Pad net (/ARCHITECTURE/DIGITAL AND HMI/D-) doesn't match net given by schematic (/CIRCUIT/D-). | @(255.145 mm, 148.25 mm): Pad B7 [/ARCHITECTURE/DIGITAL AND HMI/D-] of J502 on L1 (Sig, PWR)
net_conflict | Pad net (/ARCHITECTURE/DIGITAL AND HMI/VBUS) doesn't match net given by schematic (/CIRCUIT/VBUS). | @(255.145 mm, 149.9 mm): Pad B9 [/ARCHITECTURE/DIGITAL AND HMI/VBUS] of J502 on L1 (Sig, PWR)
net_conflict | Pad net (/ARCHITECTURE/ANALOGUE INPUTS/ECG_IN) doesn't match net given by schematic (/CIRCUIT/ECG_IN). | @(170.0 mm, 117.5 mm): PTH pad 1 [/ARCHITECTURE/ANALOGUE INPUTS/ECG_IN] of J601
net_conflict | Pad net (/ARCHITECTURE/ANALOGUE INPUTS/CE_IN) doesn't match net given by schematic (/CIRCUIT/CE_IN). | @(170.0 mm, 132.5 mm): PTH pad 1 [/ARCHITECTURE/ANALOGUE INPUTS/CE_IN] of J602
net_conflict | Pad net (/ARCHITECTURE/ANALOGUE INPUTS/CO2_IN) doesn't match net given by schematic (/CIRCUIT/CO2_IN). | @(170.0 mm, 147.5 mm): PTH pad 1 [/ARCHITECTURE/ANALOGUE INPUTS/CO2_IN] of J603
net_conflict | Pad net (/ARCHITECTURE/ANALOGUE OUTPUTS/SHAKER_P) doesn't match net given by schematic (/CIRCUIT/SHAKER_P). | @(220.915 mm, 105.35 mm): PTH pad 1 [/ARCHITECTURE/ANALOGUE OUTPUTS/SHAKER_P] of J701
net_conflict | Pad net (/ARCHITECTURE/ANALOGUE OUTPUTS/SHAKER_N) doesn't match net given by schematic (/CIRCUIT/SHAKER_N). | @(223.455 mm, 105.35 mm): PTH pad 2 [/ARCHITECTURE/ANALOGUE OUTPUTS/SHAKER_N] of J701
net_conflict | Pad net (/ARCHITECTURE/POWER/GATE_RPP) doesn't match net given by schematic (/CIRCUIT/GATE_RPP). | @(244.786 mm, 110.641999 mm): Pad 1 [/ARCHITECTURE/POWER/GATE_RPP] of Q401 on L1 (Sig, PWR)
net_conflict | Pad net (/ARCHITECTURE/POWER/VBATT_FUSED) doesn't match net given by schematic (/CIRCUIT/VBATT_FUSED). | @(242.5 mm, 117.5 mm): Pad 2 [/ARCHITECTURE/POWER/VBATT_FUSED] of Q401 on L1 (Sig, PWR)
net_conflict | Pad net (/ARCHITECTURE/POWER/GATE_RPP) doesn't match net given by schematic (/CIRCUIT/GATE_RPP). | @(245.5 mm, 106.285499 mm): Pad 1 [/ARCHITECTURE/POWER/GATE_RPP] of R401 on L1 (Sig, PWR)
net_conflict | Pad net (/ARCHITECTURE/POWER/GATE_RPP) doesn't match net given by schematic (/CIRCUIT/GATE_RPP). | @(243.325 mm, 108.285499 mm): Pad 1 [/ARCHITECTURE/POWER/GATE_RPP] of R402 on L1 (Sig, PWR)
net_conflict | Pad net (/ARCHITECTURE/DIGITAL AND HMI/LED_GRN) doesn't match net given by schematic (/CIRCUIT/LED_GRN). | @(206.3018 mm, 159.325 mm): Pad 2 [/ARCHITECTURE/DIGITAL AND HMI/LED_GRN] of R501 on L1 (Sig, PWR)
net_conflict | Pad net (/ARCHITECTURE/DIGITAL AND HMI/LED_RED) doesn't match net given by schematic (/CIRCUIT/LED_RED). | @(206.3018 mm, 155.515 mm): Pad 2 [/ARCHITECTURE/DIGITAL AND HMI/LED_RED] of R502 on L1 (Sig, PWR)
net_conflict | Pad net (/ARCHITECTURE/DIGITAL AND HMI/SWCLK) doesn't match net given by schematic (/CIRCUIT/SWCLK). | @(222.280061 mm, 152.939735 mm): Pad 2 [/ARCHITECTURE/DIGITAL AND HMI/SWCLK] of R503 on L1 (Sig, PWR)
net_conflict | Pad net (/ARCHITECTURE/DIGITAL AND HMI/SWDIO) doesn't match net given by schematic (/CIRCUIT/SWDIO). | @(224.210462 mm, 152.17606 mm): Pad 2 [/ARCHITECTURE/DIGITAL AND HMI/SWDIO] of R504 on L1 (Sig, PWR)
net_conflict | Pad net (/ARCHITECTURE/DIGITAL AND HMI/~{RST}) doesn't match net given by schematic (/CIRCUIT/~{RST}). | @(226.455526 mm, 154.421126 mm): Pad 2 [/ARCHITECTURE/DIGITAL AND HMI/~{RST}] of R505 on L1 (Sig, PWR)
net_conflict | Pad net (/ARCHITECTURE/DIGITAL AND HMI/SWO) doesn't match net given by schematic (/CIRCUIT/SWO). | @(224.525125 mm, 155.184801 mm): Pad 2 [/ARCHITECTURE/DIGITAL AND HMI/SWO] of R506 on L1 (Sig, PWR)
net_conflict | Pad net (/ARCHITECTURE/DIGITAL AND HMI/XTAL) doesn't match net given by schematic (/CIRCUIT/XTAL). | @(228.286 mm, 141.609 mm): Pad 1 [/ARCHITECTURE/DIGITAL AND HMI/XTAL] of R507 on L1 (Sig, PWR)
net_conflict | Pad net (/ARCHITECTURE/DIGITAL AND HMI/OSC_OUT) doesn't match net given by schematic (/CIRCUIT/OSC_OUT). | @(228.286 mm, 143.259 mm): Pad 2 [/ARCHITECTURE/DIGITAL AND HMI/OSC_OUT] of R507 on L1 (Sig, PWR)
net_conflict | Pad net (/ARCHITECTURE/DIGITAL AND HMI/CC1) doesn't match net given by schematic (/CIRCUIT/CC1). | @(252.225 mm, 151.07 mm): Pad 2 [/ARCHITECTURE/DIGITAL AND HMI/CC1] of R509 on L1 (Sig, PWR)
net_conflict | Pad net (/ARCHITECTURE/DIGITAL AND HMI/CC2) doesn't match net given by schematic (/CIRCUIT/CC2). | @(252.225 mm, 154.245 mm): Pad 2 [/ARCHITECTURE/DIGITAL AND HMI/CC2] of R510 on L1 (Sig, PWR)
net_conflict | Pad net (/ARCHITECTURE/ANALOGUE INPUTS/ECG_IN) doesn't match net given by schematic (/CIRCUIT/ECG_IN). | @(176.675 mm, 117.5 mm): Pad 1 [/ARCHITECTURE/ANALOGUE INPUTS/ECG_IN] of R601 on L1 (Sig, PWR)
net_conflict | Pad net (/ARCHITECTURE/ANALOGUE INPUTS/ECG_LPF1_N) doesn't match net given by schematic (/CIRCUIT/ECG_LPF1_N). | @(178.325 mm, 117.5 mm): Pad 2 [/ARCHITECTURE/ANALOGUE INPUTS/ECG_LPF1_N] of R601 on L1 (Sig, PWR)
net_conflict | Pad net (/ARCHITECTURE/ANALOGUE INPUTS/CE_IN) doesn't match net given by schematic (/CIRCUIT/CE_IN). | @(176.675 mm, 132.5 mm): Pad 1 [/ARCHITECTURE/ANALOGUE INPUTS/CE_IN] of R602 on L1 (Sig, PWR)
net_conflict | Pad net (/ARCHITECTURE/ANALOGUE INPUTS/CE_BUFF_IN) doesn't match net given by schematic (/CIRCUIT/CE_BUFF_IN). | @(178.325 mm, 132.5 mm): Pad 2 [/ARCHITECTURE/ANALOGUE INPUTS/CE_BUFF_IN] of R602 on L1 (Sig, PWR)
net_conflict | Pad net (/ARCHITECTURE/ANALOGUE INPUTS/CO2_IN) doesn't match net given by schematic (/CIRCUIT/CO2_IN). | @(176.675 mm, 147.5 mm): Pad 1 [/ARCHITECTURE/ANALOGUE INPUTS/CO2_IN] of R603 on L1 (Sig, PWR)
net_conflict | Pad net (/ARCHITECTURE/ANALOGUE INPUTS/CO2_BUFF_IN) doesn't match net given by schematic (/CIRCUIT/CO2_BUFF_IN). | @(178.325 mm, 147.5 mm): Pad 2 [/ARCHITECTURE/ANALOGUE INPUTS/CO2_BUFF_IN] of R603 on L1 (Sig, PWR)
net_conflict | Pad net (/ARCHITECTURE/ANALOGUE INPUTS/ECG_LPF1) doesn't match net given by schematic (/CIRCUIT/ECG_LPF1). | @(186.63 mm, 115.955 mm): Pad 1 [/ARCHITECTURE/ANALOGUE INPUTS/ECG_LPF1] of R604 on L1 (Sig, PWR)
net_conflict | Pad net (/ARCHITECTURE/ANALOGUE INPUTS/ECG_LPF1_N) doesn't match net given by schematic (/CIRCUIT/ECG_LPF1_N). | @(186.63 mm, 117.605 mm): Pad 2 [/ARCHITECTURE/ANALOGUE INPUTS/ECG_LPF1_N] of R604 on L1 (Sig, PWR)
net_conflict | Pad net (/ARCHITECTURE/ANALOGUE INPUTS/ECG_LPF1) doesn't match net given by schematic (/CIRCUIT/ECG_LPF1). | @(189.17 mm, 121.86 mm): Pad 1 [/ARCHITECTURE/ANALOGUE INPUTS/ECG_LPF1] of R605 on L1 (Sig, PWR)
net_conflict | Pad net (/ARCHITECTURE/ANALOGUE INPUTS/ECG_SK_MID) doesn't match net given by schematic (/CIRCUIT/ECG_SK_MID). | @(189.17 mm, 123.51 mm): Pad 2 [/ARCHITECTURE/ANALOGUE INPUTS/ECG_SK_MID] of R605 on L1 (Sig, PWR)
net_conflict | Pad net (/ARCHITECTURE/ANALOGUE INPUTS/CE_BUFF) doesn't match net given by schematic (/CIRCUIT/CE_BUFF). | @(189.17 mm, 135.83 mm): Pad 1 [/ARCHITECTURE/ANALOGUE INPUTS/CE_BUFF] of R606 on L1 (Sig, PWR)
net_conflict | Pad net (/ARCHITECTURE/ANALOGUE INPUTS/CE_SK_MID) doesn't match net given by schematic (/CIRCUIT/CE_SK_MID). | @(189.17 mm, 137.48 mm): Pad 2 [/ARCHITECTURE/ANALOGUE INPUTS/CE_SK_MID] of R606 on L1 (Sig, PWR)
net_conflict | Pad net (/ARCHITECTURE/ANALOGUE INPUTS/CO2_BUFF) doesn't match net given by schematic (/CIRCUIT/CO2_BUFF). | @(203.775 mm, 150.435 mm): Pad 1 [/ARCHITECTURE/ANALOGUE INPUTS/CO2_BUFF] of R607 on L1 (Sig, PWR)
net_conflict | Pad net (/ARCHITECTURE/ANALOGUE INPUTS/CO2_SK_MID) doesn't match net given by schematic (/CIRCUIT/CO2_SK_MID). | @(203.775 mm, 152.085 mm): Pad 2 [/ARCHITECTURE/ANALOGUE INPUTS/CO2_SK_MID] of R607 on L1 (Sig, PWR)
net_conflict | Pad net (/ARCHITECTURE/ANALOGUE INPUTS/ECG_SK_MID) doesn't match net given by schematic (/CIRCUIT/ECG_SK_MID). | @(192.98 mm, 123.51 mm): Pad 1 [/ARCHITECTURE/ANALOGUE INPUTS/ECG_SK_MID] of R608 on L1 (Sig, PWR)
net_conflict | Pad net (/ARCHITECTURE/ANALOGUE INPUTS/ECG_SK_RC) doesn't match net given by schematic (/CIRCUIT/ECG_SK_RC). | @(192.98 mm, 121.86 mm): Pad 2 [/ARCHITECTURE/ANALOGUE INPUTS/ECG_SK_RC] of R608 on L1 (Sig, PWR)
net_conflict | Pad net (/ARCHITECTURE/ANALOGUE INPUTS/CE_SK_MID) doesn't match net given by schematic (/CIRCUIT/CE_SK_MID). | @(192.98 mm, 137.48 mm): Pad 1 [/ARCHITECTURE/ANALOGUE INPUTS/CE_SK_MID] of R609 on L1 (Sig, PWR)
net_conflict | Pad net (/ARCHITECTURE/ANALOGUE INPUTS/CE_SK_RC) doesn't match net given by schematic (/CIRCUIT/CE_SK_RC). | @(192.98 mm, 135.83 mm): Pad 2 [/ARCHITECTURE/ANALOGUE INPUTS/CE_SK_RC] of R609 on L1 (Sig, PWR)
net_conflict | Pad net (/ARCHITECTURE/ANALOGUE INPUTS/CO2_SK_MID) doesn't match net given by schematic (/CIRCUIT/CO2_SK_MID). | @(205.68 mm, 152.085 mm): Pad 1 [/ARCHITECTURE/ANALOGUE INPUTS/CO2_SK_MID] of R610 on L1 (Sig, PWR)
net_conflict | Pad net (/ARCHITECTURE/ANALOGUE INPUTS/CO2_SK_RC) doesn't match net given by schematic (/CIRCUIT/CO2_SK_RC). | @(205.68 mm, 150.435 mm): Pad 2 [/ARCHITECTURE/ANALOGUE INPUTS/CO2_SK_RC] of R610 on L1 (Sig, PWR)
net_conflict | Pad net (/ARCHITECTURE/ANALOGUE INPUTS/CE_SK_N) doesn't match net given by schematic (/CIRCUIT/CE_SK_N). | @(197.235 mm, 132.655 mm): Pad 2 [/ARCHITECTURE/ANALOGUE INPUTS/CE_SK_N] of R611 on L1 (Sig, PWR)
net_conflict | Pad net (/ARCHITECTURE/ANALOGUE INPUTS/CE_SK_N) doesn't match net given by schematic (/CIRCUIT/CE_SK_N). | @(195.52 mm, 132.845 mm): Pad 1 [/ARCHITECTURE/ANALOGUE INPUTS/CE_SK_N] of R612 on L1 (Sig, PWR)
net_conflict | Pad net (/ARCHITECTURE/ANALOGUE INPUTS/CE_FILT) doesn't match net given by schematic (/CIRCUIT/CE_FILT). | @(195.52 mm, 131.195 mm): Pad 2 [/ARCHITECTURE/ANALOGUE INPUTS/CE_FILT] of R612 on L1 (Sig, PWR)
net_conflict | Pad net (/ARCHITECTURE/ANALOGUE INPUTS/CO2_GAIN_N) doesn't match net given by schematic (/CIRCUIT/CO2_GAIN_N). | @(211.9284 mm, 147.45 mm): Pad 2 [/ARCHITECTURE/ANALOGUE INPUTS/CO2_GAIN_N] of R613 on L1 (Sig, PWR)
net_conflict | Pad net (/ARCHITECTURE/ANALOGUE INPUTS/ECG_FILT) doesn't match net given by schematic (/CIRCUIT/ECG_FILT). | @(195.52 mm, 117.415 mm): Pad 1 [/ARCHITECTURE/ANALOGUE INPUTS/ECG_FILT] of R614 on L1 (Sig, PWR)
net_conflict | Pad net (/ARCHITECTURE/ANALOGUE INPUTS/ECG_GAIN_N) doesn't match net given by schematic (/CIRCUIT/ECG_GAIN_N). | @(197.17 mm, 117.415 mm): Pad 2 [/ARCHITECTURE/ANALOGUE INPUTS/ECG_GAIN_N] of R614 on L1 (Sig, PWR)
net_conflict | Pad net (/ARCHITECTURE/ANALOGUE INPUTS/CE_FILT) doesn't match net given by schematic (/CIRCUIT/CE_FILT). | @(219.191963 mm, 145.330437 mm): Pad 1 [/ARCHITECTURE/ANALOGUE INPUTS/CE_FILT] of R615 on L1 (Sig, PWR)
net_conflict | Pad net (/ARCHITECTURE/ANALOGUE INPUTS/ADC_CE) doesn't match net given by schematic (ADC_CE). | @(220.358689 mm, 146.497163 mm): Pad 2 [/ARCHITECTURE/ANALOGUE INPUTS/ADC_CE] of R615 on L1 (Sig, PWR)
net_conflict | Pad net (/ARCHITECTURE/ANALOGUE INPUTS/SERVO_OUT) doesn't match net given by schematic (/CIRCUIT/SERVO_OUT). | @(202.885 mm, 114.24 mm): Pad 1 [/ARCHITECTURE/ANALOGUE INPUTS/SERVO_OUT] of R616 on L1 (Sig, PWR)
net_conflict | Pad net (/ARCHITECTURE/ANALOGUE INPUTS/ECG_GAIN_N) doesn't match net given by schematic (/CIRCUIT/ECG_GAIN_N). | @(201.235 mm, 114.24 mm): Pad 2 [/ARCHITECTURE/ANALOGUE INPUTS/ECG_GAIN_N] of R616 on L1 (Sig, PWR)
net_conflict | Pad net (/ARCHITECTURE/ANALOGUE INPUTS/CO2_GAIN_N) doesn't match net given by schematic (/CIRCUIT/CO2_GAIN_N). | @(210.125 mm, 147.45 mm): Pad 1 [/ARCHITECTURE/ANALOGUE INPUTS/CO2_GAIN_N] of R617 on L1 (Sig, PWR)
net_conflict | Pad net (/ARCHITECTURE/ANALOGUE INPUTS/CO2_OUT) doesn't match net given by schematic (/CIRCUIT/CO2_OUT). | @(210.125 mm, 145.8 mm): Pad 2 [/ARCHITECTURE/ANALOGUE INPUTS/CO2_OUT] of R617 on L1 (Sig, PWR)
footprint_symbol_mismatch | Value (R618) doesn't match symbol value (249k). | @(201.235 mm, 116.78 mm): Footprint R618
net_conflict | Pad net (/ARCHITECTURE/ANALOGUE INPUTS/ECG_GAIN_N) doesn't match net given by schematic (/CIRCUIT/ECG_GAIN_N). | @(201.235 mm, 117.605 mm): Pad 1 [/ARCHITECTURE/ANALOGUE INPUTS/ECG_GAIN_N] of R618 on L1 (Sig, PWR)
net_conflict | Pad net (/ARCHITECTURE/ANALOGUE INPUTS/ECG_OUT) doesn't match net given by schematic (/CIRCUIT/ECG_OUT). | @(201.235 mm, 115.955 mm): Pad 2 [/ARCHITECTURE/ANALOGUE INPUTS/ECG_OUT] of R618 on L1 (Sig, PWR)
net_conflict | Pad net (/ARCHITECTURE/ANALOGUE INPUTS/CO2_OUT) doesn't match net given by schematic (/CIRCUIT/CO2_OUT). | @(220.895437 mm, 144.744563 mm): Pad 1 [/ARCHITECTURE/ANALOGUE INPUTS/CO2_OUT] of R619 on L1 (Sig, PWR)
net_conflict | Pad net (/ARCHITECTURE/ANALOGUE INPUTS/ADC_CO2) doesn't match net given by schematic (ADC_CO2). | @(222.062163 mm, 143.577837 mm): Pad 2 [/ARCHITECTURE/ANALOGUE INPUTS/ADC_CO2] of R619 on L1 (Sig, PWR)
net_conflict | Pad net (/ARCHITECTURE/ANALOGUE INPUTS/ECG_OUT) doesn't match net given by schematic (/CIRCUIT/ECG_OUT). | @(226.051637 mm, 143.501637 mm): Pad 1 [/ARCHITECTURE/ANALOGUE INPUTS/ECG_OUT] of R620 on L1 (Sig, PWR)
net_conflict | Pad net (/ARCHITECTURE/ANALOGUE INPUTS/ADC_ECG) doesn't match net given by schematic (ADC_ECG). | @(227.218363 mm, 144.668363 mm): Pad 2 [/ARCHITECTURE/ANALOGUE INPUTS/ADC_ECG] of R620 on L1 (Sig, PWR)
net_conflict | Pad net (/ARCHITECTURE/ANALOGUE INPUTS/SERVO_N) doesn't match net given by schematic (/CIRCUIT/SERVO_N). | @(212.665 mm, 119.765 mm): Pad 1 [/ARCHITECTURE/ANALOGUE INPUTS/SERVO_N] of R621 on L1 (Sig, PWR)
net_conflict | Pad net (/ARCHITECTURE/ANALOGUE INPUTS/SERVO_P) doesn't match net given by schematic (/CIRCUIT/SERVO_P). | @(208.855 mm, 121.225 mm): Pad 1 [/ARCHITECTURE/ANALOGUE INPUTS/SERVO_P] of R622 on L1 (Sig, PWR)
net_conflict | Pad net (/ARCHITECTURE/ANALOGUE INPUTS/ECG_OUT) doesn't match net given by schematic (/CIRCUIT/ECG_OUT). | @(208.855 mm, 122.875 mm): Pad 2 [/ARCHITECTURE/ANALOGUE INPUTS/ECG_OUT] of R622 on L1 (Sig, PWR)
net_conflict | Pad net (/ARCHITECTURE/ANALOGUE OUTPUTS/DAC_SHAKER) doesn't match net given by schematic (DAC_SHAKER). | @(212.92 mm, 127.575 mm): Pad 1 [/ARCHITECTURE/ANALOGUE OUTPUTS/DAC_SHAKER] of R701 on L1 (Sig, PWR)
net_conflict | Pad net (/ARCHITECTURE/ANALOGUE OUTPUTS/SHK_SK1_MID) doesn't match net given by schematic (/CIRCUIT/SHK_SK1_MID). | @(214.57 mm, 127.575 mm): Pad 2 [/ARCHITECTURE/ANALOGUE OUTPUTS/SHK_SK1_MID] of R701 on L1 (Sig, PWR)
net_conflict | Pad net (/ARCHITECTURE/ANALOGUE OUTPUTS/SHK_SK1_MID) doesn't match net given by schematic (/CIRCUIT/SHK_SK1_MID). | @(216.095 mm, 127.575 mm): Pad 1 [/ARCHITECTURE/ANALOGUE OUTPUTS/SHK_SK1_MID] of R702 on L1 (Sig, PWR)
net_conflict | Pad net (/ARCHITECTURE/ANALOGUE OUTPUTS/SHK_SK1_RC) doesn't match net given by schematic (/CIRCUIT/SHK_SK1_RC). | @(217.745 mm, 127.575 mm): Pad 2 [/ARCHITECTURE/ANALOGUE OUTPUTS/SHK_SK1_RC] of R702 on L1 (Sig, PWR)
net_conflict | Pad net (/ARCHITECTURE/ANALOGUE OUTPUTS/SHK_FILT1) doesn't match net given by schematic (/CIRCUIT/SHK_FILT1). | @(221.365 mm, 130.75 mm): Pad 1 [/ARCHITECTURE/ANALOGUE OUTPUTS/SHK_FILT1] of R703 on L1 (Sig, PWR)
net_conflict | Pad net (/ARCHITECTURE/ANALOGUE OUTPUTS/SHK_SK2_MID) doesn't match net given by schematic (/CIRCUIT/SHK_SK2_MID). | @(223.015 mm, 130.75 mm): Pad 2 [/ARCHITECTURE/ANALOGUE OUTPUTS/SHK_SK2_MID] of R703 on L1 (Sig, PWR)
net_conflict | Pad net (/ARCHITECTURE/ANALOGUE OUTPUTS/SHK_SK2_MID) doesn't match net given by schematic (/CIRCUIT/SHK_SK2_MID). | @(228.285 mm, 129.48 mm): Pad 1 [/ARCHITECTURE/ANALOGUE OUTPUTS/SHK_SK2_MID] of R704 on L1 (Sig, PWR)
net_conflict | Pad net (/ARCHITECTURE/ANALOGUE OUTPUTS/SHK_SK2_RC) doesn't match net given by schematic (/CIRCUIT/SHK_SK2_RC). | @(226.635 mm, 129.48 mm): Pad 2 [/ARCHITECTURE/ANALOGUE OUTPUTS/SHK_SK2_RC] of R704 on L1 (Sig, PWR)
net_conflict | Pad net (/ARCHITECTURE/ANALOGUE OUTPUTS/VREF_SHK) doesn't match net given by schematic (/CIRCUIT/VREF_SHK). | @(221.81 mm, 112.335 mm): Pad 1 [/ARCHITECTURE/ANALOGUE OUTPUTS/VREF_SHK] of R705 on L1 (Sig, PWR)
net_conflict | Pad net (/ARCHITECTURE/ANALOGUE OUTPUTS/VREF_SHK) doesn't match net given by schematic (/CIRCUIT/VREF_SHK). | @(220.285 mm, 112.335 mm): Pad 2 [/ARCHITECTURE/ANALOGUE OUTPUTS/VREF_SHK] of R706 on L1 (Sig, PWR)
net_conflict | Pad net (/ARCHITECTURE/ANALOGUE OUTPUTS/SHK_FILT2) doesn't match net given by schematic (/CIRCUIT/SHK_FILT2). | @(221.365 mm, 121.86 mm): Pad 1 [/ARCHITECTURE/ANALOGUE OUTPUTS/SHK_FILT2] of R707 on L1 (Sig, PWR)
net_conflict | Pad net (/ARCHITECTURE/ANALOGUE OUTPUTS/SHK_N) doesn't match net given by schematic (/CIRCUIT/SHK_N). | @(223.015 mm, 121.86 mm): Pad 2 [/ARCHITECTURE/ANALOGUE OUTPUTS/SHK_N] of R707 on L1 (Sig, PWR)
net_conflict | Pad net (/ARCHITECTURE/ANALOGUE OUTPUTS/SHAKER_N) doesn't match net given by schematic (/CIRCUIT/SHAKER_N). | @(226.635 mm, 117.225 mm): Pad 1 [/ARCHITECTURE/ANALOGUE OUTPUTS/SHAKER_N] of R708 on L1 (Sig, PWR)
net_conflict | Pad net (/ARCHITECTURE/ANALOGUE OUTPUTS/SHK_N) doesn't match net given by schematic (/CIRCUIT/SHK_N). | @(226.635 mm, 118.875 mm): Pad 2 [/ARCHITECTURE/ANALOGUE OUTPUTS/SHK_N] of R708 on L1 (Sig, PWR)
net_conflict | Pad net (/ARCHITECTURE/ANALOGUE OUTPUTS/SHAKER_P) doesn't match net given by schematic (/CIRCUIT/SHAKER_P). | @(221.2634 mm, 107.89 mm): Pad 1 [/ARCHITECTURE/ANALOGUE OUTPUTS/SHAKER_P] of R709 on L1 (Sig, PWR)
net_conflict | Pad net (/ARCHITECTURE/ANALOGUE OUTPUTS/SHAKER_N) doesn't match net given by schematic (/CIRCUIT/SHAKER_N). | @(222.9134 mm, 107.89 mm): Pad 2 [/ARCHITECTURE/ANALOGUE OUTPUTS/SHAKER_N] of R709 on L1 (Sig, PWR)
net_conflict | Pad net (/ARCHITECTURE/DIGITAL AND HMI/BTN) doesn't match net given by schematic (/CIRCUIT/BTN). | @(188.075 mm, 159.905 mm): Pad 2 [/ARCHITECTURE/DIGITAL AND HMI/BTN] of SW501 on L1 (Sig, PWR)
net_conflict | Pad net (/ARCHITECTURE/DIGITAL AND HMI/BTN) doesn't match net given by schematic (/CIRCUIT/BTN). | @(194.075 mm, 159.905 mm): Pad 2 [/ARCHITECTURE/DIGITAL AND HMI/BTN] of SW501 on L1 (Sig, PWR)
net_conflict | Pad net (/ARCHITECTURE/POWER/VBATT_RAW) doesn't match net given by schematic (/CIRCUIT/VBATT_RAW). | @(252.67 mm, 127.575 mm): Pad 1 [/ARCHITECTURE/POWER/VBATT_RAW] of TP401 on L1 (Sig, PWR)
net_conflict | Pad net (/ARCHITECTURE/ANALOGUE INPUTS/ECG_FILT) doesn't match net given by schematic (/CIRCUIT/ECG_FILT). | @(199.33 mm, 109.16 mm): PTH pad 1 [/ARCHITECTURE/ANALOGUE INPUTS/ECG_FILT] of TP601
net_conflict | Pad net (/ARCHITECTURE/ANALOGUE INPUTS/CE_FILT) doesn't match net given by schematic (/CIRCUIT/CE_FILT). | @(199.33 mm, 126.94 mm): PTH pad 1 [/ARCHITECTURE/ANALOGUE INPUTS/CE_FILT] of TP602
net_conflict | Pad net (/ARCHITECTURE/ANALOGUE INPUTS/CO2_OUT) doesn't match net given by schematic (/CIRCUIT/CO2_OUT). | @(199.33 mm, 139.64 mm): PTH pad 1 [/ARCHITECTURE/ANALOGUE INPUTS/CO2_OUT] of TP603
net_conflict | Pad net (/ARCHITECTURE/ANALOGUE INPUTS/ECG_OUT) doesn't match net given by schematic (/CIRCUIT/ECG_OUT). | @(212.665 mm, 109.16 mm): PTH pad 1 [/ARCHITECTURE/ANALOGUE INPUTS/ECG_OUT] of TP604
net_conflict | Pad net (/ARCHITECTURE/DIGITAL AND HMI/OSC_IN) doesn't match net given by schematic (/CIRCUIT/OSC_IN). | @(230.177043 mm, 144.163616 mm): Pad 2 [/ARCHITECTURE/DIGITAL AND HMI/OSC_IN] of U501 on L1 (Sig, PWR)
net_conflict | Pad net (/ARCHITECTURE/DIGITAL AND HMI/OSC_OUT) doesn't match net given by schematic (/CIRCUIT/OSC_OUT). | @(229.611357 mm, 144.729301 mm): Pad 3 [/ARCHITECTURE/DIGITAL AND HMI/OSC_OUT] of U501 on L1 (Sig, PWR)
net_conflict | Pad net (/ARCHITECTURE/DIGITAL AND HMI/~{RST}) doesn't match net given by schematic (/CIRCUIT/~{RST}). | @(229.045672 mm, 145.294986 mm): Pad 4 [/ARCHITECTURE/DIGITAL AND HMI/~{RST}] of U501 on L1 (Sig, PWR)
net_conflict | Pad net (/ARCHITECTURE/ANALOGUE INPUTS/ADC_ECG) doesn't match net given by schematic (ADC_ECG). | @(228.479986 mm, 145.860672 mm): Pad 5 [/ARCHITECTURE/ANALOGUE INPUTS/ADC_ECG] of U501 on L1 (Sig, PWR)
net_conflict | Pad net (/ARCHITECTURE/ANALOGUE INPUTS/ADC_CO2) doesn't match net given by schematic (ADC_CO2). | @(227.914301 mm, 146.426357 mm): Pad 6 [/ARCHITECTURE/ANALOGUE INPUTS/ADC_CO2] of U501 on L1 (Sig, PWR)
net_conflict | Pad net (/ARCHITECTURE/ANALOGUE OUTPUTS/DAC_SHAKER) doesn't match net given by schematic (DAC_SHAKER). | @(226.78293 mm, 149.502272 mm): Pad 9 [/ARCHITECTURE/ANALOGUE OUTPUTS/DAC_SHAKER] of U501 on L1 (Sig, PWR)
net_conflict | Pad net (/ARCHITECTURE/ANALOGUE INPUTS/ADC_CE) doesn't match net given by schematic (ADC_CE). | @(228.479986 mm, 151.199328 mm): Pad 12 [/ARCHITECTURE/ANALOGUE INPUTS/ADC_CE] of U501 on L1 (Sig, PWR)
net_conflict | Pad net (/ARCHITECTURE/DIGITAL AND HMI/VDDA) doesn't match net given by schematic (VDDA). | @(230.177043 mm, 152.896384 mm): Pad 15 [/ARCHITECTURE/DIGITAL AND HMI/VDDA] of U501 on L1 (Sig, PWR)
net_conflict | Pad net (/ARCHITECTURE/DIGITAL AND HMI/BTN) doesn't match net given by schematic (/CIRCUIT/BTN). | @(233.252957 mm, 152.896384 mm): Pad 18 [/ARCHITECTURE/DIGITAL AND HMI/BTN] of U501 on L1 (Sig, PWR)
net_conflict | Pad net (/ARCHITECTURE/DIGITAL AND HMI/LED_RED) doesn't match net given by schematic (/CIRCUIT/LED_RED). | @(233.818643 mm, 152.330699 mm): Pad 19 [/ARCHITECTURE/DIGITAL AND HMI/LED_RED] of U501 on L1 (Sig, PWR)
net_conflict | Pad net (/ARCHITECTURE/DIGITAL AND HMI/LED_GRN) doesn't match net given by schematic (/CIRCUIT/LED_GRN). | @(234.384328 mm, 151.765014 mm): Pad 20 [/ARCHITECTURE/DIGITAL AND HMI/LED_GRN] of U501 on L1 (Sig, PWR)
net_conflict | Pad net (/ARCHITECTURE/DIGITAL AND HMI/A-) doesn't match net given by schematic (/CIRCUIT/A-). | @(234.950014 mm, 151.199328 mm): Pad 21 [/ARCHITECTURE/DIGITAL AND HMI/A-] of U501 on L1 (Sig, PWR)
net_conflict | Pad net (/ARCHITECTURE/DIGITAL AND HMI/A+) doesn't match net given by schematic (/CIRCUIT/A+). | @(235.515699 mm, 150.633643 mm): Pad 22 [/ARCHITECTURE/DIGITAL AND HMI/A+] of U501 on L1 (Sig, PWR)
net_conflict | Pad net (/ARCHITECTURE/DIGITAL AND HMI/SWDIO) doesn't match net given by schematic (/CIRCUIT/SWDIO). | @(236.081384 mm, 150.067957 mm): Pad 23 [/ARCHITECTURE/DIGITAL AND HMI/SWDIO] of U501 on L1 (Sig, PWR)
net_conflict | Pad net (/ARCHITECTURE/DIGITAL AND HMI/SWCLK) doesn't match net given by schematic (/CIRCUIT/SWCLK). | @(236.64707 mm, 149.502272 mm): Pad 24 [/ARCHITECTURE/DIGITAL AND HMI/SWCLK] of U501 on L1 (Sig, PWR)
net_conflict | Pad net (/ARCHITECTURE/DIGITAL AND HMI/SWO) doesn't match net given by schematic (/CIRCUIT/SWO). | @(236.081384 mm, 146.992043 mm): Pad 26 [/ARCHITECTURE/DIGITAL AND HMI/SWO] of U501 on L1 (Sig, PWR)
net_conflict | Pad net (/ARCHITECTURE/DIGITAL AND HMI/D-) doesn't match net given by schematic (/CIRCUIT/D-). | @(248.6375 mm, 148.449999 mm): Pad 1 [/ARCHITECTURE/DIGITAL AND HMI/D-] of U502 on L1 (Sig, PWR)
net_conflict | Pad net (/ARCHITECTURE/DIGITAL AND HMI/D+) doesn't match net given by schematic (/CIRCUIT/D+). | @(248.6375 mm, 146.550001 mm): Pad 3 [/ARCHITECTURE/DIGITAL AND HMI/D+] of U502 on L1 (Sig, PWR)
net_conflict | Pad net (/ARCHITECTURE/DIGITAL AND HMI/A+) doesn't match net given by schematic (/CIRCUIT/A+). | @(246.3625 mm, 146.550001 mm): Pad 4 [/ARCHITECTURE/DIGITAL AND HMI/A+] of U502 on L1 (Sig, PWR)
net_conflict | Pad net (/ARCHITECTURE/DIGITAL AND HMI/A-) doesn't match net given by schematic (/CIRCUIT/A-). | @(246.3625 mm, 148.449999 mm): Pad 6 [/ARCHITECTURE/DIGITAL AND HMI/A-] of U502 on L1 (Sig, PWR)
net_conflict | Pad net (/ARCHITECTURE/ANALOGUE INPUTS/CO2_BUFF) doesn't match net given by schematic (/CIRCUIT/CO2_BUFF). | @(188.6 mm, 144.72 mm): Pad 1 [/ARCHITECTURE/ANALOGUE INPUTS/CO2_BUFF] of U601 on L1 (Sig, PWR)
net_conflict | Pad net (/ARCHITECTURE/ANALOGUE INPUTS/CO2_BUFF) doesn't match net given by schematic (/CIRCUIT/CO2_BUFF). | @(188.6 mm, 145.99 mm): Pad 2 [/ARCHITECTURE/ANALOGUE INPUTS/CO2_BUFF] of U601 on L1 (Sig, PWR)
net_conflict | Pad net (/ARCHITECTURE/ANALOGUE INPUTS/CO2_BUFF_IN) doesn't match net given by schematic (/CIRCUIT/CO2_BUFF_IN). | @(188.6 mm, 147.26 mm): Pad 3 [/ARCHITECTURE/ANALOGUE INPUTS/CO2_BUFF_IN] of U601 on L1 (Sig, PWR)
net_conflict | Pad net (/ARCHITECTURE/ANALOGUE INPUTS/CO2_FILT) doesn't match net given by schematic (/CIRCUIT/CO2_FILT). | @(203.205 mm, 144.72 mm): Pad 1 [/ARCHITECTURE/ANALOGUE INPUTS/CO2_FILT] of U602 on L1 (Sig, PWR)
net_conflict | Pad net (/ARCHITECTURE/ANALOGUE INPUTS/CO2_FILT) doesn't match net given by schematic (/CIRCUIT/CO2_FILT). | @(203.205 mm, 145.99 mm): Pad 2 [/ARCHITECTURE/ANALOGUE INPUTS/CO2_FILT] of U602 on L1 (Sig, PWR)
net_conflict | Pad net (/ARCHITECTURE/ANALOGUE INPUTS/CO2_SK_RC) doesn't match net given by schematic (/CIRCUIT/CO2_SK_RC). | @(203.205 mm, 147.26 mm): Pad 3 [/ARCHITECTURE/ANALOGUE INPUTS/CO2_SK_RC] of U602 on L1 (Sig, PWR)
net_conflict | Pad net (/ARCHITECTURE/ANALOGUE INPUTS/CO2_FILT) doesn't match net given by schematic (/CIRCUIT/CO2_FILT). | @(208.155 mm, 148.53 mm): Pad 5 [/ARCHITECTURE/ANALOGUE INPUTS/CO2_FILT] of U602 on L1 (Sig, PWR)
net_conflict | Pad net (/ARCHITECTURE/ANALOGUE INPUTS/CO2_GAIN_N) doesn't match net given by schematic (/CIRCUIT/CO2_GAIN_N). | @(208.155 mm, 147.26 mm): Pad 6 [/ARCHITECTURE/ANALOGUE INPUTS/CO2_GAIN_N] of U602 on L1 (Sig, PWR)
net_conflict | Pad net (/ARCHITECTURE/ANALOGUE INPUTS/CO2_OUT) doesn't match net given by schematic (/CIRCUIT/CO2_OUT). | @(208.155 mm, 145.99 mm): Pad 7 [/ARCHITECTURE/ANALOGUE INPUTS/CO2_OUT] of U602 on L1 (Sig, PWR)
net_conflict | Pad net (/ARCHITECTURE/ANALOGUE INPUTS/CE_BUFF) doesn't match net given by schematic (/CIRCUIT/CE_BUFF). | @(188.6 mm, 130.115 mm): Pad 1 [/ARCHITECTURE/ANALOGUE INPUTS/CE_BUFF] of U603 on L1 (Sig, PWR)
net_conflict | Pad net (/ARCHITECTURE/ANALOGUE INPUTS/CE_BUFF) doesn't match net given by schematic (/CIRCUIT/CE_BUFF). | @(188.6 mm, 131.385 mm): Pad 2 [/ARCHITECTURE/ANALOGUE INPUTS/CE_BUFF] of U603 on L1 (Sig, PWR)
net_conflict | Pad net (/ARCHITECTURE/ANALOGUE INPUTS/CE_BUFF_IN) doesn't match net given by schematic (/CIRCUIT/CE_BUFF_IN). | @(188.6 mm, 132.655 mm): Pad 3 [/ARCHITECTURE/ANALOGUE INPUTS/CE_BUFF_IN] of U603 on L1 (Sig, PWR)
net_conflict | Pad net (/ARCHITECTURE/ANALOGUE INPUTS/CE_SK_RC) doesn't match net given by schematic (/CIRCUIT/CE_SK_RC). | @(193.55 mm, 133.925 mm): Pad 5 [/ARCHITECTURE/ANALOGUE INPUTS/CE_SK_RC] of U603 on L1 (Sig, PWR)
net_conflict | Pad net (/ARCHITECTURE/ANALOGUE INPUTS/CE_SK_N) doesn't match net given by schematic (/CIRCUIT/CE_SK_N). | @(193.55 mm, 132.655 mm): Pad 6 [/ARCHITECTURE/ANALOGUE INPUTS/CE_SK_N] of U603 on L1 (Sig, PWR)
net_conflict | Pad net (/ARCHITECTURE/ANALOGUE INPUTS/CE_FILT) doesn't match net given by schematic (/CIRCUIT/CE_FILT). | @(193.55 mm, 131.385 mm): Pad 7 [/ARCHITECTURE/ANALOGUE INPUTS/CE_FILT] of U603 on L1 (Sig, PWR)
net_conflict | Pad net (/ARCHITECTURE/ANALOGUE INPUTS/ECG_LPF1) doesn't match net given by schematic (/CIRCUIT/ECG_LPF1). | @(188.6 mm, 116.145 mm): Pad 1 [/ARCHITECTURE/ANALOGUE INPUTS/ECG_LPF1] of U604 on L1 (Sig, PWR)
net_conflict | Pad net (/ARCHITECTURE/ANALOGUE INPUTS/ECG_LPF1_N) doesn't match net given by schematic (/CIRCUIT/ECG_LPF1_N). | @(188.6 mm, 117.415 mm): Pad 2 [/ARCHITECTURE/ANALOGUE INPUTS/ECG_LPF1_N] of U604 on L1 (Sig, PWR)
net_conflict | Pad net (/ARCHITECTURE/ANALOGUE INPUTS/ECG_SK_RC) doesn't match net given by schematic (/CIRCUIT/ECG_SK_RC). | @(193.55 mm, 119.955 mm): Pad 5 [/ARCHITECTURE/ANALOGUE INPUTS/ECG_SK_RC] of U604 on L1 (Sig, PWR)
net_conflict | Pad net (/ARCHITECTURE/ANALOGUE INPUTS/ECG_FILT) doesn't match net given by schematic (/CIRCUIT/ECG_FILT). | @(193.55 mm, 118.685 mm): Pad 6 [/ARCHITECTURE/ANALOGUE INPUTS/ECG_FILT] of U604 on L1 (Sig, PWR)
net_conflict | Pad net (/ARCHITECTURE/ANALOGUE INPUTS/ECG_FILT) doesn't match net given by schematic (/CIRCUIT/ECG_FILT). | @(193.55 mm, 117.415 mm): Pad 7 [/ARCHITECTURE/ANALOGUE INPUTS/ECG_FILT] of U604 on L1 (Sig, PWR)
net_conflict | Pad net (/ARCHITECTURE/ANALOGUE INPUTS/ECG_OUT) doesn't match net given by schematic (/CIRCUIT/ECG_OUT). | @(203.205 mm, 116.145 mm): Pad 1 [/ARCHITECTURE/ANALOGUE INPUTS/ECG_OUT] of U605 on L1 (Sig, PWR)
net_conflict | Pad net (/ARCHITECTURE/ANALOGUE INPUTS/ECG_GAIN_N) doesn't match net given by schematic (/CIRCUIT/ECG_GAIN_N). | @(203.205 mm, 117.415 mm): Pad 2 [/ARCHITECTURE/ANALOGUE INPUTS/ECG_GAIN_N] of U605 on L1 (Sig, PWR)
net_conflict | Pad net (/ARCHITECTURE/ANALOGUE INPUTS/SERVO_P) doesn't match net given by schematic (/CIRCUIT/SERVO_P). | @(208.155 mm, 119.955 mm): Pad 5 [/ARCHITECTURE/ANALOGUE INPUTS/SERVO_P] of U605 on L1 (Sig, PWR)
net_conflict | Pad net (/ARCHITECTURE/ANALOGUE INPUTS/SERVO_N) doesn't match net given by schematic (/CIRCUIT/SERVO_N). | @(208.155 mm, 118.685 mm): Pad 6 [/ARCHITECTURE/ANALOGUE INPUTS/SERVO_N] of U605 on L1 (Sig, PWR)
net_conflict | Pad net (/ARCHITECTURE/ANALOGUE INPUTS/SERVO_OUT) doesn't match net given by schematic (/CIRCUIT/SERVO_OUT). | @(208.155 mm, 117.415 mm): Pad 7 [/ARCHITECTURE/ANALOGUE INPUTS/SERVO_OUT] of U605 on L1 (Sig, PWR)
net_conflict | Pad net (/ARCHITECTURE/ANALOGUE OUTPUTS/SHK_FILT1) doesn't match net given by schematic (/CIRCUIT/SHK_FILT1). | @(219.715 mm, 125.035 mm): Pad 1 [/ARCHITECTURE/ANALOGUE OUTPUTS/SHK_FILT1] of U701 on L1 (Sig, PWR)
net_conflict | Pad net (/ARCHITECTURE/ANALOGUE OUTPUTS/SHK_FILT1) doesn't match net given by schematic (/CIRCUIT/SHK_FILT1). | @(219.715 mm, 126.305 mm): Pad 2 [/ARCHITECTURE/ANALOGUE OUTPUTS/SHK_FILT1] of U701 on L1 (Sig, PWR)
net_conflict | Pad net (/ARCHITECTURE/ANALOGUE OUTPUTS/SHK_SK1_RC) doesn't match net given by schematic (/CIRCUIT/SHK_SK1_RC). | @(219.715 mm, 127.575 mm): Pad 3 [/ARCHITECTURE/ANALOGUE OUTPUTS/SHK_SK1_RC] of U701 on L1 (Sig, PWR)
net_conflict | Pad net (/ARCHITECTURE/ANALOGUE OUTPUTS/SHK_SK2_RC) doesn't match net given by schematic (/CIRCUIT/SHK_SK2_RC). | @(224.665 mm, 128.845 mm): Pad 5 [/ARCHITECTURE/ANALOGUE OUTPUTS/SHK_SK2_RC] of U701 on L1 (Sig, PWR)
net_conflict | Pad net (/ARCHITECTURE/ANALOGUE OUTPUTS/SHK_FILT2) doesn't match net given by schematic (/CIRCUIT/SHK_FILT2). | @(224.665 mm, 127.575 mm): Pad 6 [/ARCHITECTURE/ANALOGUE OUTPUTS/SHK_FILT2] of U701 on L1 (Sig, PWR)
net_conflict | Pad net (/ARCHITECTURE/ANALOGUE OUTPUTS/SHK_FILT2) doesn't match net given by schematic (/CIRCUIT/SHK_FILT2). | @(224.665 mm, 126.305 mm): Pad 7 [/ARCHITECTURE/ANALOGUE OUTPUTS/SHK_FILT2] of U701 on L1 (Sig, PWR)
net_conflict | Pad net (/ARCHITECTURE/ANALOGUE OUTPUTS/SHAKER_P) doesn't match net given by schematic (/CIRCUIT/SHAKER_P). | @(219.715 mm, 116.145 mm): Pad 1 [/ARCHITECTURE/ANALOGUE OUTPUTS/SHAKER_P] of U702 on L1 (Sig, PWR)
net_conflict | Pad net (/ARCHITECTURE/ANALOGUE OUTPUTS/SHAKER_P) doesn't match net given by schematic (/CIRCUIT/SHAKER_P). | @(219.715 mm, 117.415 mm): Pad 2 [/ARCHITECTURE/ANALOGUE OUTPUTS/SHAKER_P] of U702 on L1 (Sig, PWR)
net_conflict | Pad net (/ARCHITECTURE/ANALOGUE OUTPUTS/SHK_FILT2) doesn't match net given by schematic (/CIRCUIT/SHK_FILT2). | @(219.715 mm, 118.685 mm): Pad 3 [/ARCHITECTURE/ANALOGUE OUTPUTS/SHK_FILT2] of U702 on L1 (Sig, PWR)
net_conflict | Pad net (/ARCHITECTURE/ANALOGUE OUTPUTS/VREF_SHK) doesn't match net given by schematic (/CIRCUIT/VREF_SHK). | @(224.665 mm, 119.955 mm): Pad 5 [/ARCHITECTURE/ANALOGUE OUTPUTS/VREF_SHK] of U702 on L1 (Sig, PWR)
net_conflict | Pad net (/ARCHITECTURE/ANALOGUE OUTPUTS/SHK_N) doesn't match net given by schematic (/CIRCUIT/SHK_N). | @(224.665 mm, 118.685 mm): Pad 6 [/ARCHITECTURE/ANALOGUE OUTPUTS/SHK_N] of U702 on L1 (Sig, PWR)
net_conflict | Pad net (/ARCHITECTURE/ANALOGUE OUTPUTS/SHAKER_N) doesn't match net given by schematic (/CIRCUIT/SHAKER_N). | @(224.665 mm, 117.415 mm): Pad 7 [/ARCHITECTURE/ANALOGUE OUTPUTS/SHAKER_N] of U702 on L1 (Sig, PWR)
net_conflict | Pad net (/ARCHITECTURE/DIGITAL AND HMI/OSC_IN) doesn't match net given by schematic (/CIRCUIT/OSC_IN). | @(231.615001 mm, 135.83 mm): PTH pad 1 [/ARCHITECTURE/DIGITAL AND HMI/OSC_IN] of Y501
net_conflict | Pad net (/ARCHITECTURE/DIGITAL AND HMI/XTAL) doesn't match net given by schematic (/CIRCUIT/XTAL). | @(226.735001 mm, 135.83 mm): PTH pad 2 [/ARCHITECTURE/DIGITAL AND HMI/XTAL] of Y501

Generated by KiBot (https://github.com/INTI-CMNB/KiBot/) v1.8.6

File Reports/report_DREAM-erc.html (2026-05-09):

Logo

(https://github.com/INTI-CMNB/KiBot/) | ERC report for DREAM
| Schematic: DREAM Revision: 1.2.0 Date: 2026-05-09T09:53:00+0000 KiCad Version: 9.0.7 | Errors: 0 Warnings: 15 Total: 15

Sheet / (DREAM.kicad_sch)

Type | Description | Details
footprint_link_issues | The current configuration does not include the footprint library 'RD-Testpoints'. | @(0.6477 mm, 0.5334 mm): Symbol TP401 [TestPoint]
footprint_link_issues | The current configuration does not include the footprint library 'RD-Testpoints'. | @(1.2573 mm, 0.5461 mm): Symbol TP402 [TestPoint]
footprint_link_issues | The current configuration does not include the footprint library 'RD-Testpoints'. | @(1.0922 mm, 1.27 mm): Symbol TP501 [TestPoint]
footprint_link_issues | The current configuration does not include the footprint library 'RD-Testpoints'. | @(2.0193 mm, 0.762 mm): Symbol TP403 [TestPoint]
footprint_link_issues | The current configuration does not include the footprint library 'RD-Testpoints'. | @(1.651 mm, 2.4257 mm): Symbol TP601 [TestPoint_PMK_Probe]
lib_symbol_issues | The current configuration does not include the symbol library 'Ryan-Dynamics' | @(1.651 mm, 2.4257 mm): Symbol TP601 [TestPoint_PMK_Probe]
footprint_link_issues | The current configuration does not include the footprint library 'RD-Testpoints'. | @(2.032 mm, 2.4003 mm): Symbol TP604 [TestPoint_PMK_Probe]
lib_symbol_issues | The current configuration does not include the symbol library 'Ryan-Dynamics' | @(2.032 mm, 2.4003 mm): Symbol TP604 [TestPoint_PMK_Probe]
footprint_link_issues | The current configuration does not include the footprint library 'RD-Testpoints'. | @(1.651 mm, 3.1369 mm): Symbol TP602 [TestPoint_PMK_Probe]
lib_symbol_issues | The current configuration does not include the symbol library 'Ryan-Dynamics' | @(1.651 mm, 3.1369 mm): Symbol TP602 [TestPoint_PMK_Probe]
footprint_link_issues | The current configuration does not include the footprint library 'RD-Testpoints'. | @(0.7366 mm, 3.7338 mm): Symbol TP404 [TestPoint]
footprint_link_issues | The current configuration does not include the footprint library 'RD-Testpoints'. | @(3.7973 mm, 0.8382 mm): Symbol TP603 [TestPoint_PMK_Probe]
lib_symbol_issues | The current configuration does not include the symbol library 'Ryan-Dynamics' | @(3.7973 mm, 0.8382 mm): Symbol TP603 [TestPoint_PMK_Probe]
footprint_link_issues | The current configuration does not include the footprint library 'RD-Symbols-Silkscreen'. | @(1.6891 mm, 3.6449 mm): Symbol ID401 [BOARD_STACKUP_MARKER]
lib_symbol_issues | The current configuration does not include the symbol library 'Ryan-Dynamics' | @(1.6891 mm, 3.6449 mm): Symbol ID401 [BOARD_STACKUP_MARKER]

Generated by KiBot (https://github.com/INTI-CMNB/KiBot/) v1.8.6

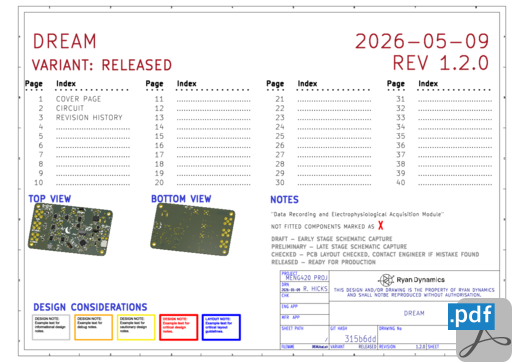
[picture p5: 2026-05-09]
HTML/images/cat_pdf_schematic_DREAM-schematic.png

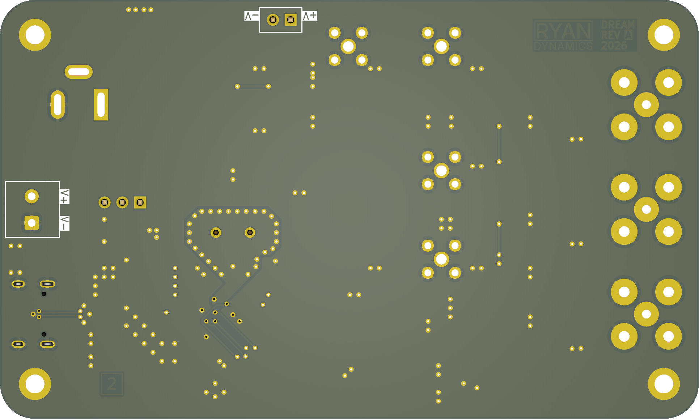
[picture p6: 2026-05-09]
Images/DREAM-bottom.png

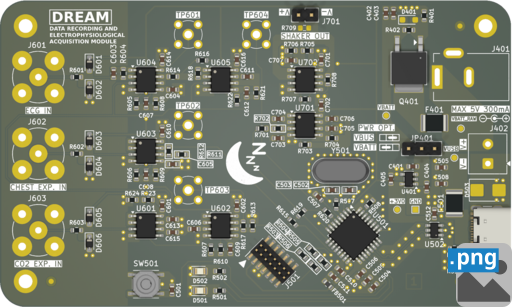
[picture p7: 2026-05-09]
HTML/images/cat_png_3d_viewer_top_DREAM-top.png

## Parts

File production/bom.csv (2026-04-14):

Designator | Footprint | Quantity | Value | LCSC Part #
C401, C403, C501, C506, C507, C508, C509, C512, C601, C602, C604, C610, C613, C614, C616, C701, C702, C707 | 0603 | 18 | 100n | C1608X7R1C104KT
C402, C505, C611, C612 | 0603 | 4 | 10u | C1608X7R0J106KT
C404, C405, C511, C603, C615 | 0603 | 5 | 1u | C1608X5R0J105KT
C502, C503 | 0603 | 2 | 27p | C1608COG1H270JT
C504 | 0603 | 1 | 4.7u | C1608X5R0J475MT
C510, C705 | 0603 | 2 | 10n | C1608X7R1H103KT
C605, C607, C608, C609 | 0603 | 4 | 390n | C1608X5R1A394KT
C606 | 0603 | 1 | 180n | C1608X5R1A184KT
C703 | 0603 | 1 | 15n | C1608X7R1H153KT
C704 | 0603 | 1 | 18n | C1608X7R1C183KT
C706 | 0603 | 1 | 68n | C1608X7R1C683KT
D401 | D_SOD-323_HandSoldering | 1 | D3Z10BF-7 | D3Z10BF-7
D501 | 0805 | 1 | LED | LTST-C170KGKT
D502 | 0805 | 1 | LED | LTST-C170KRKT
D601, D602, D603, D604, D605, D606 | D_SOD-323_HandSoldering | 6 | 1N4148WS | 1N4148WS
F401, F501 | 1812 | 2 | MF-MSMF030-2 | Bourns Inc.
FB501 | 0603 | 1 | MH1608-601Y | MH1608-601Y
J401 | BarrelJack_Kycon_KLDX-0202-xC_Horizontal | 1 | KLDX-0202-B | KLDX-0202-B
J402 | TerminalBlock_Phoenix_MKDS-1-2-3.81_1x02_P3.81mm_Horizontal | 1 | EBWA-02-B | EBWA-02-B
J501 | PinHeader_2x07_P1.27mm_Vertical_SMD | 1 | Conn_ST_STDC14
J502 | USB_C_Receptacle_GCT_USB4105-xx-A_16P_TopMnt_Horizontal | 1 | USB4105-GF-A | USB4105-GF-A
J601, J602, J603 | BNC_TEConnectivity_1478204_Vertical | 3 | 1-1337535-0 | 1-1337535-0
J701 | PinHeader_1x02_P2.54mm_Vertical | 1 | PH1-02-UA
Q401 | DPAK_MCC | 1 | MCU18P10Y-TP | MCU18P10Y-TP
R401, R402 | 0603 | 2 | 100k
R501, R502, R601, R602, R603, R604 | 0603 | 6 | 1k
R503, R504, R505, R506 | 0603 | 4 | 22.1
R507 | 0603 | 1 | 0
R508, R611, R613, R614, R624, R706, R707, R708 | 0603 | 8 | 10k
R509, R510, R605, R608 | 0603 | 4 | 5.11k
R606, R609 | 0603 | 2 | 27.4k
R607 | 0603 | 1 | 11k
R610, R617, R705 | 0603 | 3 | 20k
R612 | 0603 | 1 | 5.62k
R615, R619, R620, R709 | 0603 | 4 | 100
R616 | 0603 | 1 | 18.2k
R618 | 0603 | 1 | 249k
R621, R622 | 0603 | 2 | 2.2M
R623 | 0603 | 1 | 39.2k
R701, R702 | 0603 | 2 | 12.1k
R703, R704 | 0603 | 2 | 7.5k
SW501 | SW_SPST_PTS526xxxSMTR | 1 | PTS526SK15SMTR2 LFS | PTS526SK15SMTR2 LFS
U401 | SOT-23-5 | 1 | TPS7A2030PDBVR | TPS7A2030PDBVR
U501 | LQFP-32_7x7mm_P0.8mm | 1 | STM32G441KBT6 | STM32G441KBT6
U502 | SOT-23-6 | 1 | USBLC6-2SC6 | USBLC6-2SC6
U601, U602, U604, U605 | SOIC-8_3.9x4.9mm_P1.27mm | 4 | TSV912AIDR | TSV912AIDR
U603, U701, U702 | SOIC-8_3.9x4.9mm_P1.27mm | 3 | LM358LVIDR | LM358LVIDR
Y501 | Crystal_HC49-4H_Vertical | 1 | ATS08A-E | ATS08A-E

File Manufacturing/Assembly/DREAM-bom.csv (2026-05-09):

Row | Quantity Per PCB | References | Value | Datasheet | Footprint | Description | Manufacturer | MPN | Supplier | SPN | Notes
1 | 2 | C502 C503 | 27p | https://mm.digikey.com/Volume0/opasdata/d220001/medias/docus/931/C_Series_GeneralAppl_B11.pdf | C_0603_1608Metric | CAP CER 27PF 50V NP0 0603 | TPK | C1608COG1H270JT
2 | 2 | C510 C705 | 10n | https://mm.digikey.com/Volume0/opasdata/d220001/medias/docus/931/C_Series_GeneralAppl_B11.pdf | C_0603_1608Metric | CAP CER 10N 50V X7R 0603 | TPK | C1608X7R1H103KT
3 | 1 | C703 | 15n | https://mm.digikey.com/Volume0/opasdata/d220001/medias/docus/931/C_Series_GeneralAppl_B11.pdf | C_0603_1608Metric | CAP CER 15N 50V X7R 0603 | TPK | C1608X7R1H153KT
4 | 1 | C704 | 18n | https://mm.digikey.com/Volume0/opasdata/d220001/medias/docus/931/C_Series_GeneralAppl_B11.pdf | C_0603_1608Metric | CAP CER 18N 16V X7R 0603 | TPK | C1608X7R1C183KT
5 | 1 | C706 | 68n | https://mm.digikey.com/Volume0/opasdata/d220001/medias/docus/931/C_Series_GeneralAppl_B11.pdf | C_0603_1608Metric | CAP CER 68N 16V X7R 0603 | TPK | C1608X7R1C683KT
6 | 18 | C401 C403 C501 C506 C507 C508 C509 C512 C601 C602 C604 C610 C613 C614 C616 C701 C702 C707 | 100n | https://mm.digikey.com/Volume0/opasdata/d220001/medias/docus/931/C_Series_GeneralAppl_B11.pdf | C_0603_1608Metric | CAP CER 100N 16V X7R 0603 | TPK | C1608X7R1C104KT
7 | 1 | C606 | 180n | https://mm.digikey.com/Volume0/opasdata/d220001/medias/docus/931/C_Series_GeneralAppl_B11.pdf | C_0603_1608Metric | CAP CER 180N 10V X5R 0603 | TPK | C1608X5R1A184KT
8 | 4 | C605 C607 C608 C609 | 390n | https://mm.digikey.com/Volume0/opasdata/d220001/medias/docus/931/C_Series_GeneralAppl_B11.pdf | C_0603_1608Metric | CAP CER 390N 10V X5R 0603 | TPK | C1608X5R1A394KT
9 | 5 | C404 C405 C511 C603 C615 | 1u | https://mm.digikey.com/Volume0/opasdata/d220001/medias/docus/931/C_Series_GeneralAppl_B11.pdf | C_0603_1608Metric | CAP CER 1U 6.3V X5R 0603 | TPK | C1608X5R0J105KT
10 | 1 | C504 | 4.7u | https://mm.digikey.com/Volume0/opasdata/d220001/medias/docus/931/C_Series_GeneralAppl_B11.pdf | C_0603_1608Metric | CAP CER 4.7U 6.3V X5R 0603 | TPK | C1608X5R0J475MT
11 | 4 | C402 C505 C611 C612 | 10u | https://mm.digikey.com/Volume0/opasdata/d220001/medias/docus/931/C_Series_GeneralAppl_B11.pdf | C_0603_1608Metric | CAP CER 10U 6.3V X7R 0603 | TPK | C1608X7R0J106KT
12 | 6 | D601 D602 D603 D604 D605 D606 | 1N4148WS | https://www.vishay.com/docs/85751/1n4148ws.pdf | D_SOD-323_HandSoldering | DIODE STANDARD 75V 150MA SOD323 | Diotec Semiconductor | 1N4148WS | DigiKey | 5245-1N4148WSTR-ND
13 | 1 | D501 | LED | https://optoelectronics.liteon.com/upload/download/DS22-2000-073/LTST-C170KGKT.pdf | LED_0805_2012Metric | LED GRN CLEAR SMD | Lite-On Inc. | LTST-C170KGKT | DigiKey | 160-1414-1-ND | Any low power green 0805 LED
14 | 1 | D502 | LED | https://optoelectronics.liteon.com/upload/download/DS-22-99-0150/LTST-C170KRKT.pdf | LED_0805_2012Metric | LED RED CLEAR SMD | Lite-On Inc. | LTST-C170KRKT | DigiKey | 160-1415-1-ND | Any low power red 0805 LED
15 | 2 | F401 F501 | MF-MSMF030-2 | https://www.bourns.com/docs/product-datasheets/mf-msmf.pdf | R_1812_4532Metric | PTC RESET FUSE 30V 300MA 1812 | Bourns Inc. | Bourns Inc. | DigiKey | MF-MSMF030-2CT-ND
16 | 1 | FB501 | BLM18KG101JH1D | https://pim.murata.com/asset/pim4/ferriteBeadInductortypefilter/QNFA9129_PDF_FERRITEBEADINDUCTORTYPEFILTER?lastModifiedDatetime=20250918112959 | L_0603_1608Metric | FERRITE BEAD 100 OHM 0603 4LN | Murata Electronics | BLM18KG101JH1D | DigiKey | 490-14024-1-ND
17 | 3 | J601 J602 J603 | 1-1337535-0 | https://www.te.com/commerce/DocumentDelivery/DDEController?Action=srchrtrv&DocNm=1337535&DocType=Customer+Drawing&DocLang=English | BNC_TEConnectivity_1478204_Vertical | CONN BNC JACK STR 50 OHM PCB | TE Connectivity AMP Connectors | 1-1337535-0 | DigiKey | 1-1337535-0-ND
18 | 1 | J501 | 20021121-00014T1LF | https://www.st.com/content/ccc/resource/technical/document/user_manual/group1/99/49/91/b6/b2/3a/46/e5/DM00526767/files/DM00526767.pdf/jcr:content/translations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 | PinHeader_2x07_P1.27mm_Vertical_SMD | ST Debug Connector, standard ARM Cortex-M SWD and JTAG interface plus UART | Amphenol ICC (FCI) | 20021121-00014T1LF | DigiKey | 20021121-00014T1LF-ND
19 | 1 | J402 | EBWA-02-B | https://app.adam-tech.com/products/download/data_sheet/204240/ebwa-xx-b-data-sheet.pdf | TerminalBlock_Phoenix_MKDS-1-2-3.81_1x02_P3.81mm_Horizontal | EURO BLOCK 2P | Adam Tech | EBWA-02-B | DigiKey | 2057-EBWA-02-B-ND
20 | 2 | J401 J701 | KLDX-0202-B | https://www.kycon.com/Catalog_PDF/KLDX_0202.pdf | BarrelJack_Kycon_KLDX-0202-xC_Horizontal | CONN PWR JACK 2.5X5.5MM SOLDER HEADER 2PIN 2.54MM THT | Kycon, Inc. Adam Tech | KLDX-0202-B | DigiKey | 2092-KLDX-0202-B-ND
21 | 1 | J502 | USB4105-GF-A | https://gct.co/files/specs/usb4105-spec.pdf | USB_C_Receptacle_GCT_USB4105-xx-A_16P_TopMnt_Horizontal | CONN RCP USB2.0 TYP C 16P SMD RA | GCT | USB4105-GF-A | DigiKey | 2073-USB4105-GF-ACT-ND
22 | 1 | Q401 | MCU18P10Y-TP | https://www.mccsemi.com/pdf/Products/MCU18P10Y(DPAK).pdf | DPAK_MCC | MOSFET P-CH 100V 18A DPAK | MCC (Micro Commercial Components) | MCU18P10Y-TP |  |  | VDS > 100 V, ID > 2 A, P-channel device suitable for high-side switching
23 | 1 | R507 | 0 | https://www.analogtechnologies.com/document/New_Resistor_Kits.pdf | R_0603_1608Metric | RES 0 OHM 1% 1/10W 0603 | Analog Technologies
24 | 4 | R503 R504 R505 R506 | 22.1 | https://www.analogtechnologies.com/document/New_Resistor_Kits.pdf | R_0603_1608Metric | RES 22.1 OHM 1% 1/10W 0603 | Analog Technologies
25 | 3 | R615 R619 R620 | 100 | https://www.analogtechnologies.com/document/New_Resistor_Kits.pdf | R_0603_1608Metric | RES 100 OHM 1% 1/10W 0603 | Analog Technologies
26 | 6 | R501 R502 R601 R602 R603 R604 | 1k | https://www.analogtechnologies.com/document/New_Resistor_Kits.pdf | R_0603_1608Metric | RES 1K OHM 1% 1/10W 0603 | Analog Technologies
27 | 4 | R509 R510 R605 R608 | 5.11k | https://www.analogtechnologies.com/document/New_Resistor_Kits.pdf | R_0603_1608Metric | RES 5.11K OHM 1% 1/10W 0603 | Analog Technologies
28 | 1 | R612 | 5.62k | https://www.analogtechnologies.com/document/New_Resistor_Kits.pdf | R_0603_1608Metric | RES 5.62K OHM 1% 1/10W 0603 | Analog Technologies
29 | 2 | R703 R704 | 7.5k | https://www.analogtechnologies.com/document/New_Resistor_Kits.pdf | R_0603_1608Metric | RES 7.5K OHM 1% 1/10W 0603 | Analog Technologies
30 | 8 | R508 R611 R613 R614 R624 R706 R707 R708 | 10k | https://www.analogtechnologies.com/document/New_Resistor_Kits.pdf | R_0603_1608Metric | RES 10K OHM 1% 1/10W 0603 | Analog Technologies
31 | 1 | R607 | 11k | https://www.analogtechnologies.com/document/New_Resistor_Kits.pdf | R_0603_1608Metric | RES 11K OHM 1% 1/10W 0603 | Analog Technologies
32 | 2 | R701 R702 | 12.1k | https://www.analogtechnologies.com/document/New_Resistor_Kits.pdf | R_0603_1608Metric | RES 12.1K OHM 1% 1/10W 0603 | Analog Technologies
33 | 1 | R616 | 18.2k | https://www.analogtechnologies.com/document/New_Resistor_Kits.pdf | R_0603_1608Metric | RES 18.2K OHM 1% 1/10W 0603 | Analog Technologies
34 | 3 | R610 R617 R705 | 20k | https://www.analogtechnologies.com/document/New_Resistor_Kits.pdf | R_0603_1608Metric | RES 20K OHM 1% 1/10W 0603 | Analog Technologies
35 | 2 | R606 R609 | 27.4k | https://www.analogtechnologies.com/document/New_Resistor_Kits.pdf | R_0603_1608Metric | RES 27.4K OHM 1% 1/10W 0603 | Analog Technologies
36 | 1 | R623 | 39.2k | https://www.analogtechnologies.com/document/New_Resistor_Kits.pdf | R_0603_1608Metric | RES 39.2K OHM 1% 1/10W 0603 | Analog Technologies
37 | 3 | R401 R402 R618 | 100k | https://www.analogtechnologies.com/document/New_Resistor_Kits.pdf | R_0603_1608Metric | RES 100K OHM 1% 1/10W 0603 RES 249K OHM 1% 1/10W 0603 | Analog Technologies
38 | 2 | R621 R622 | 2.2M | https://www.analogtechnologies.com/document/New_Resistor_Kits.pdf | R_0603_1608Metric | RES 2.2M OHM 1% 1/10W 0603 | Analog Technologies
39 | 1 | SW501 | PTS526SK15SMTR2 LFS | https://www.littelfuse.com/assetdocs/littelfuse-c-k-tactile-pts526-series-datasheet?assetguid=bb56c1b4-71ca-4262-9bd7-cf3e3c572bb3 | SW_SPST_PTS526xxxSMTR | SWITCH TACTILE SPST-NO 0.05A 12V | C&K | PTS526SK15SMTR2 LFS | DigiKey | CKN12221-1-ND
40 | 3 | U603 U701 U702 | LM358LVIDR | https://www.ti.com/general/docs/suppproductinfo.tsp?distId=10&gotoUrl=https://www.ti.com/lit/gpn/lm324lv | SOIC-8_3.9x4.9mm_P1.27mm | IC OPAMP GP 2 CIRCUIT 8SOIC | Texas Instruments | LM358LVIDR | DigiKey | 296-51267-1-ND
41 | 1 | U501 | STM32G441KBT6 | https://www.st.com/resource/en/datasheet/stm32g441cb.pdf | LQFP-32_7x7mm_P0.8mm | IC MCU 32BIT 128KB FLASH 32LQFP | STMicroelectronics | STM32G441KBT6 | DigiKey | 497-STM32G441KBT6-ND
42 | 1 | U401 | TPS7A2030PDBVR | https://www.ti.com/general/docs/suppproductinfo.tsp?distId=10&gotoUrl=http://www.ti.com/lit/gpn/tps7a20 | SOT-23-5 | IC REG LINEAR 3V 300MA SOT23-5 | Texas Instruments | TPS7A2030PDBVR | DigiKey | 296-TPS7A2030PDBVRCT-ND
43 | 4 | U601 U602 U604 U605 | TSV912AIDR | https://www.ti.com/general/docs/suppproductinfo.tsp?distId=10&gotoUrl=https://www.ti.com/lit/gpn/tsv912 | SOIC-8_3.9x4.9mm_P1.27mm | IC OPAMP GP 2 CIRCUIT 8SOIC | Texas Instruments | TSV912AIDR | DigiKey | 296-47162-1-ND
44 | 1 | U502 | USBLC6-2SC6 | https://www.st.com/resource/en/datasheet/cd00050750.pdf | SOT-23-6 | TVS DIODE 5.25VWM 17VC SOT23-6 | STMicroelectronics | USBLC6-2SC6 | DigiKey | 497-5235-1-ND
45 | 1 | Y501 | ATS08A-E | https://www.ctscorp.com/Files/DataSheets/Passives/FCP/Crystals/crystals-ATS-ATSSM-datasheet.pdf | Crystal_HC49-4H_Vertical | CRYSTAL 8.0000MHZ 20PF TH | CTS-Frequency Controls | ATS08A-E | DigiKey | CTX1054-ND

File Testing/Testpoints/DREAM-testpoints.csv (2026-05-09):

Testpoint Ref. | Net | Net Class | X | Y | Side | Pad Type | Value | Footprint
TP401 | /ARCHITECTURE/POWER/VBATT_RAW | Power VBATT | 90.1700 | 34.9250 | top |  | VBATT_RAW | TestPoint_Pad_D1.0mm
TP402 | VBATT | Power VBATT | 75.5650 | 37.4650 | top |  | VBATT | TestPoint_Pad_D1.0mm
TP403 | +3V0 | Power 3V0 | 77.7240 | 19.0500 | top |  | +3V0 | TestPoint_Pad_D1.0mm
TP404 | GND | GND | 81.2800 | 19.0500 | top |  | GND | TestPoint_Pad_1.0x1.0mm
TP501 | VUSB | Power VBUS | 88.9000 | 29.2100 | top |  | VUSB | TestPoint_Pad_D1.0mm
TP601 | GND,/ARCHITECTURE/ANALOGUE INPUTS/ECG_FILT | Default,GND | 36.8300 | 53.3400 | top | THRU | TestPoint_PMK_Probe | TestPoint_THTPad_PMK
TP602 | /ARCHITECTURE/ANALOGUE INPUTS/CE_FILT,GND | Default,GND | 36.8300 | 35.5600 | top | THRU | TestPoint_PMK_Probe | TestPoint_THTPad_PMK
TP603 | GND,/ARCHITECTURE/ANALOGUE INPUTS/CO2_OUT | Default,GND | 36.8300 | 22.8600 | top | THRU | TestPoint_PMK_Probe | TestPoint_THTPad_PMK
TP604 | /ARCHITECTURE/ANALOGUE INPUTS/ECG_OUT,GND | Default,GND | 50.1650 | 53.3400 | top | THRU | TestPoint_PMK_Probe | TestPoint_THTPad_PMK

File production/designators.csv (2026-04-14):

C401:1
C402:1
C403:1
C404:1
C405:1
C501:1
C502:1
C503:1
C504:1
C505:1
C506:1
C507:1
C508:1
C509:1
C510:1
C511:1
C512:1
C601:1
C602:1
C603:1
C604:1
C605:1
C606:1
C607:1
C608:1
C609:1
C610:1
C611:1
C612:1
C613:1
C614:1
C615:1
C616:1
C701:1
C702:1
C703:1
C704:1
C705:1
C706:1
C707:1
D401:1
D501:1
D502:1
D503:1
D601:1
D602:1
D603:1
D604:1
D605:1
D606:1
F401:1
F501:1
FB501:1
FID401:1
FID402:1
FID403:1
H401:1
H402:1
H403:1
H404:1
ID401:1
J401:1
J402:1
J501:1
J502:1
J601:1
J602:1
J603:1
J701:1
JP401:1
Q401:1
R401:1
R402:1
R501:1
R502:1
R503:1
R504:1
R505:1
R506:1
R507:1
R508:1
R509:1
R510:1
R601:1
R602:1
R603:1
R604:1
R605:1
R606:1
R607:1
R608:1
R609:1
R610:1
R611:1
R612:1
R613:1
R614:1
R615:1
R616:1
R617:1
R618:1
R619:1
R620:1
R621:1
R622:1
R623:1
R624:1
R701:1
R702:1
R703:1
R704:1
R705:1
R706:1
R707:1
R708:1
R709:1
SW501:1
TP401:1
TP402:1
TP403:1
TP404:1
TP501:1
TP601:1
TP602:1
TP603:1
TP604:1
U401:1
U501:1
U502:1
U601:1
U602:1
U603:1
U604:1
U605:1
U701:1
U702:1
Y501:1

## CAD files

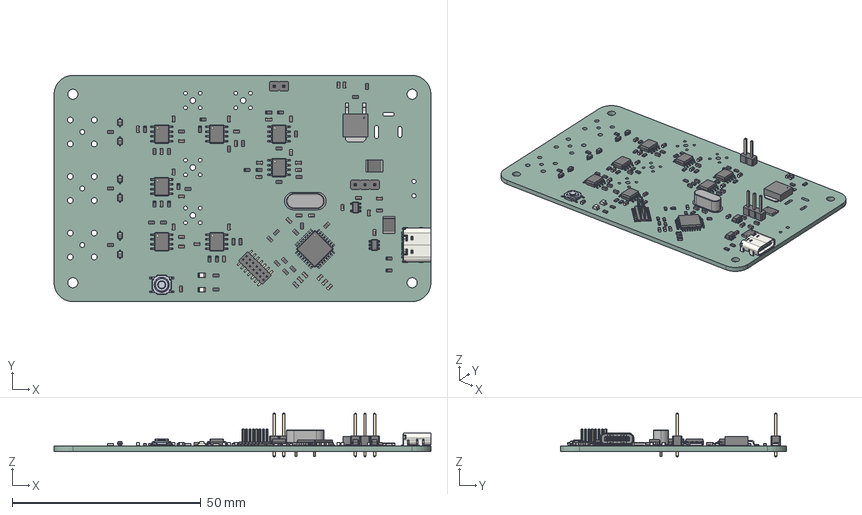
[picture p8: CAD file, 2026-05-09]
3D/DREAM.step
100.0 x 60.0 x 11.5 mm
SOT-23-6
R_0603_1608Metric x 44
D_SOD-323 x 6
PinHeader_1x03_P2.54mm_Vertical
C_0603_1608Metric x 40
L_0603_1608Metric
SOIC-8_3.9x4.9mm_P1.27mm x 7
R_1812_4532Metric x 2
LQFP-32_7x7mm_P0.8mm
LED_0805_2012Metric x 2
PinHeader_1x02_P2.54mm_Vertical
SOT-23-5
DPAK_MCC
PTS526SK15SMTR2LFS
USB_C_Receptacle_GCT_USB4105-xx-A_16P_TopMnt_Horizontal
PinHeader_2x07_P1.27mm_Vertical_SMD
Crystal_HC49-4H_Vertical
kibot_9jydoc1t_PCB

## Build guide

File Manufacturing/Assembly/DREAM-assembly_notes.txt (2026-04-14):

ASSEMBLY NOTES (UNLESS OTHERWISE SPECIFIED)

1)	DO NOT POPULATE PARTS ARE MARKED WITH A RED CROSS.

2)	DO NOT POPULATE PARTS ARE NOT PRESENT IN THE BOM.

3)	IF CONFLICTING INFORMATION IS FOUND BETWEEN THE ASSEMBLY
	FILE AND BOM, BOM SHOULD BE USED AS THE MAIN SOURCE.

4)	CONFORMAL COATING IS NOT REQUIRED.

5)	DOT IDENTIFIES PIN #1 LOCATION AND DEVICE ORIENTATION
	WHEN VIEWED FROM THE TOP.

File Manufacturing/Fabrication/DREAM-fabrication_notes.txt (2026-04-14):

FABRICATION NOTES (UNLESS OTHERWISE SPECIFIED)

1)	FABRICATE PER IPC-6012A CLASS 2.

2)	OUTLINE DEFINED IN SEPARATE GERBER FILE WITH
	"Edge_Cuts.GBR" SUFFIX.

3)	SEE SEPARATE DRILL FILES WITH ".DRL" SUFFIX 
	FOR HOLE LOCATIONS.

	SELECTED HOLE LOCATIONS SHOWN ON THIS DRAWING 
	FOR REFERENCE ONLY.

4)	SURFACE FINISH: IMMERSION GOLD

5)	SOLDERMASK ON BOTH SIDES OF THE BOARD SHALL 
	BE LPI, COLOR GREEN.

6)	SILK SCREEN LEGEND TO BE APPLIED PER LAYER 
	STACKUP USING WHITE NON-CONDUCTIVE EPOXY INK.

7)	ALL VIAS ARE TO BE NON-TENTED.

8)	VENDOR SHOULD FOLLOW ROHS COMPLIANT PROCESS 
	AND Pb FREE FOR MANUFACTURING

9)	PCB MATERIAL REQUIREMENTS:

	A.	FLAMMABILITY RATING MUST MEET OR EXCEED 
		UL94V-0 REQUIREMENTS.
	B.	Tg 170 C OR EQUIVALENT.
	C.	EQUIVALENT MATERIAL SHALL BE RoHS COMPLIANT, 
		HALOGEN FREE AND APPROVED BY RYAN DYNAMICS.

10)	DESIGN GEOMETRY MINIMUM FEATURE SIZES:

	BOARD SIZE				100.000 × 60.000 mm
	BOARD THICKNESS		1.600 mm
	TRACE WIDTH			0.200 mm
	TRACE TO TRACE		0.200 mm
	MIN. HOLE (PTH)			0.300 mm
	MIN. HOLE (NPTH)		0.650 mm
	ANNULAR RING			0.150 mm
	COPPER TO HOLE		0.254 mm
	COPPER TO EDGE		0.250 mm
	HOLE TO HOLE			0.254 mm

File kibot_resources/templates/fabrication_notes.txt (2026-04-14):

FABRICATION NOTES (UNLESS OTHERWISE SPECIFIED)

1)	FABRICATE PER IPC-6012A CLASS 2.

2)	OUTLINE DEFINED IN SEPARATE GERBER FILE WITH
	"Edge_Cuts.GBR" SUFFIX.

3)	SEE SEPARATE DRILL FILES WITH ".DRL" SUFFIX 
	FOR HOLE LOCATIONS.

	SELECTED HOLE LOCATIONS SHOWN ON THIS DRAWING 
	FOR REFERENCE ONLY.

4)	SURFACE FINISH: ${pcb_finish_cap}

5)	SOLDERMASK ON BOTH SIDES OF THE BOARD SHALL 
	BE LPI, COLOR ${solder_mask_color_text_cap}.

6)	SILK SCREEN LEGEND TO BE APPLIED PER LAYER 
	STACKUP USING ${silk_screen_color_text_cap} NON-CONDUCTIVE EPOXY INK.

7)	ALL VIAS ARE TO BE NON-TENTED.

8)	VENDOR SHOULD FOLLOW ROHS COMPLIANT PROCESS 
	AND Pb FREE FOR MANUFACTURING

9)	PCB MATERIAL REQUIREMENTS:

	A.	FLAMMABILITY RATING MUST MEET OR EXCEED 
		UL94V-0 REQUIREMENTS.
	B.	Tg 170 C OR EQUIVALENT.
	C.	EQUIVALENT MATERIAL SHALL BE RoHS COMPLIANT, 
		HALOGEN FREE AND APPROVED BY ${COMPANY_cap}.

10)	DESIGN GEOMETRY MINIMUM FEATURE SIZES:

	BOARD SIZE				${bb_w_mm} × ${bb_h_mm} mm
	BOARD THICKNESS		${thickness_mm} mm
	TRACE WIDTH			${track_mm} mm
	TRACE TO TRACE		${clearance_mm} mm
	MIN. HOLE (PTH)			${drill_pth_real_mm} mm
	MIN. HOLE (NPTH)		${drill_npth_real_mm} mm
	ANNULAR RING			${oar_mm} mm
	COPPER TO HOLE		${c2h_mm} mm
	COPPER TO EDGE		${c2e_mm} mm
	HOLE TO HOLE			${h2h_mm} mm
#?stackup and impedance_controlled

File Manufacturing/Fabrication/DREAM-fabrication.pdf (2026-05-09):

# TOP FABRICATION (SCALE 1:1)

# DREAM FABRICATION DOCUMENT

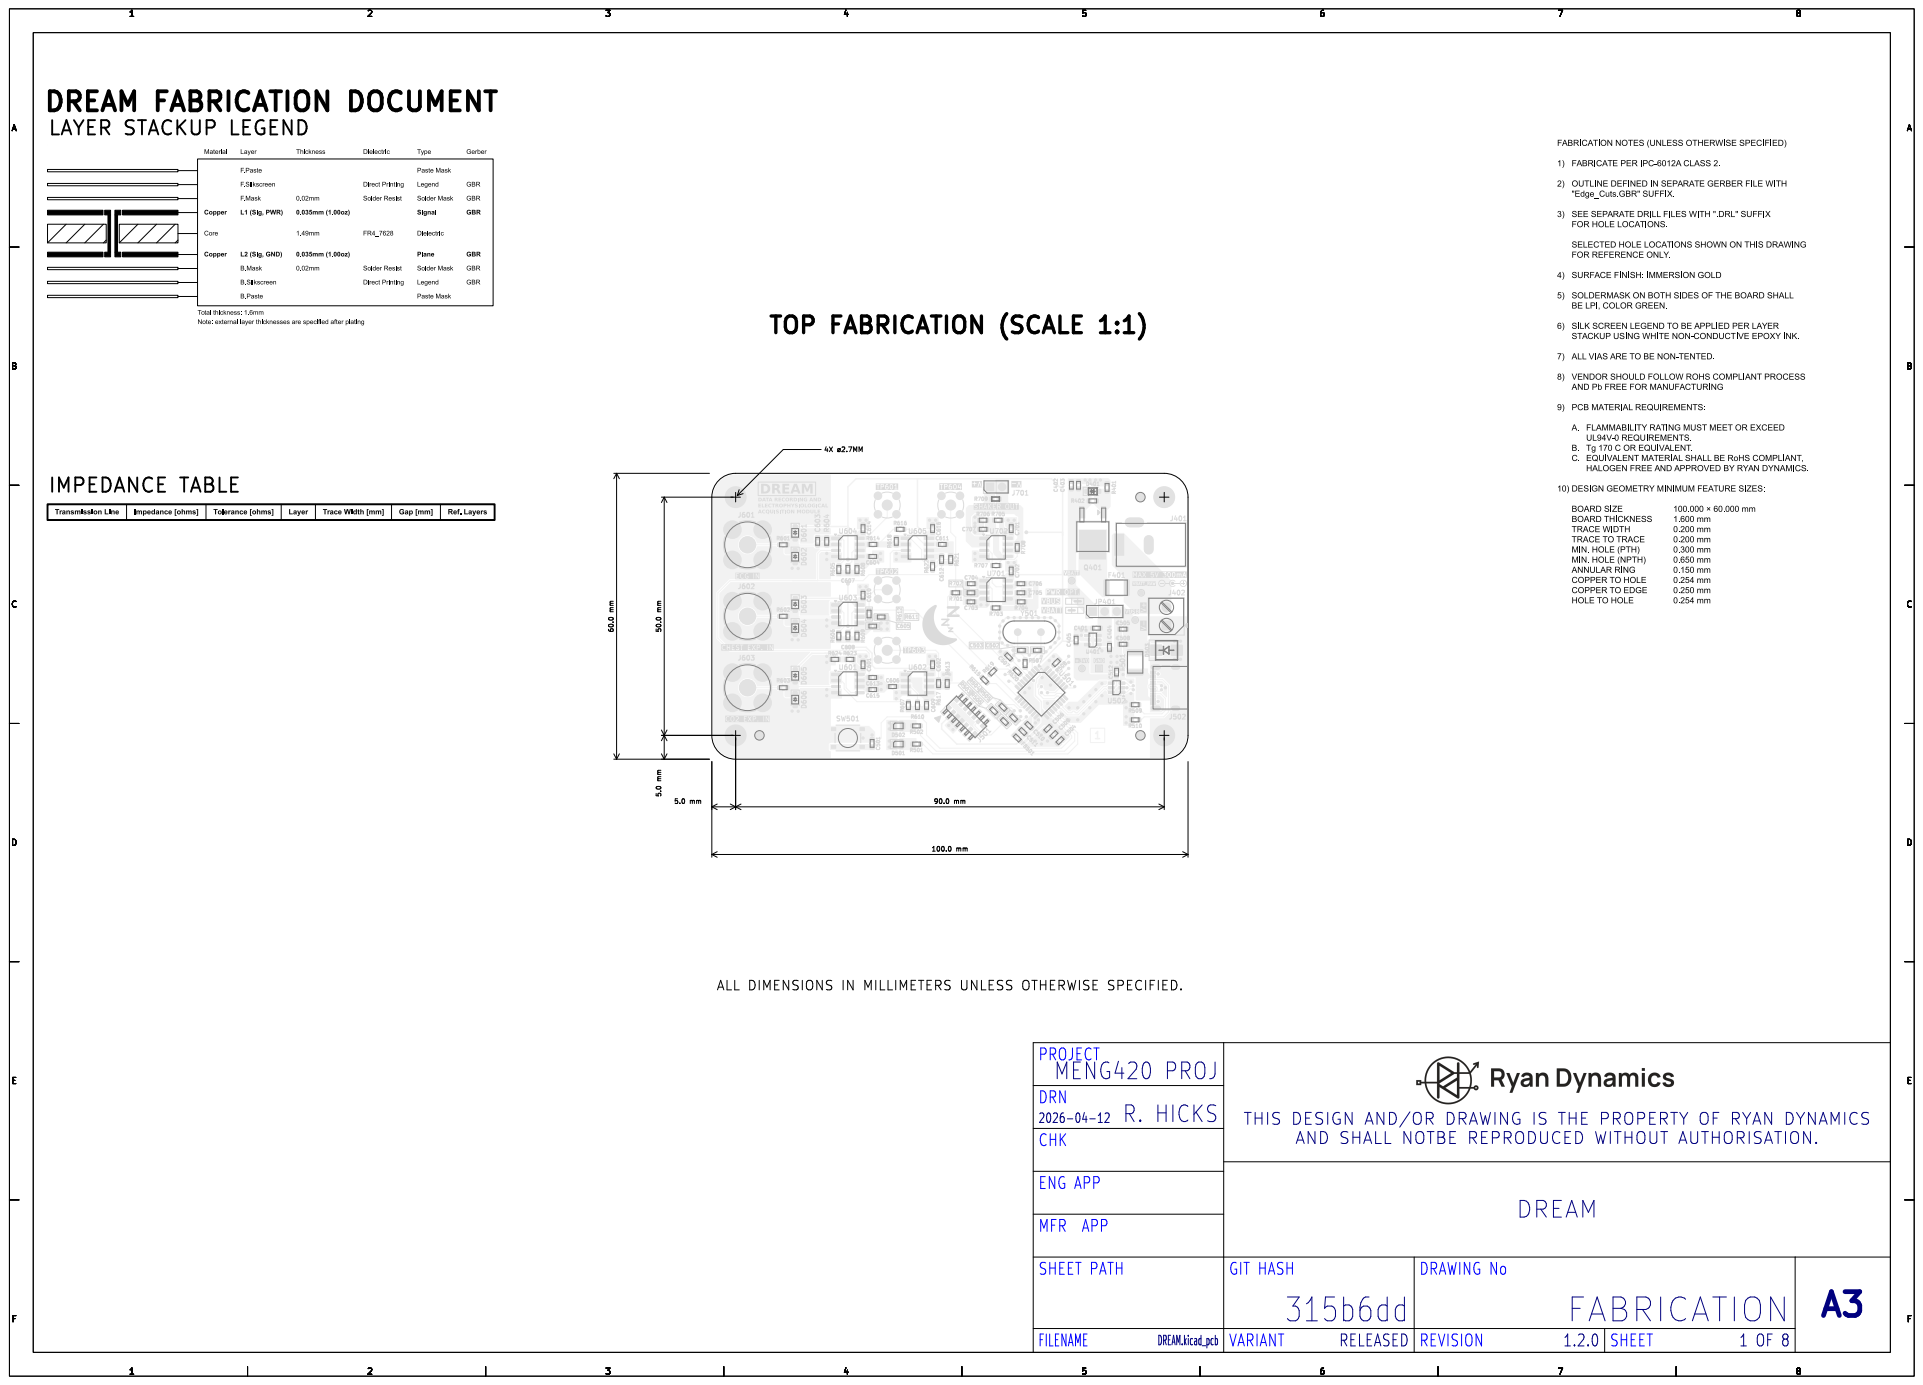
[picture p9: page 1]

ALL DIMENSIONS IN MILLIMETERS UNLESS OTHERWISE SPECIFIED.

PROJECT
MENG420 PROJ
DRN
THIS DESIGN AND/OR DRAWING IS THE PROPERTY OF RYAN DYNAMICSAND SHALL NOTBE REPRODUCED WITHOUT AUTHORISATION.
CHK

BOTTOM | FABRICATION | (SCALE | 1:1)
DREAM | FABRICATION | DOCUMENT

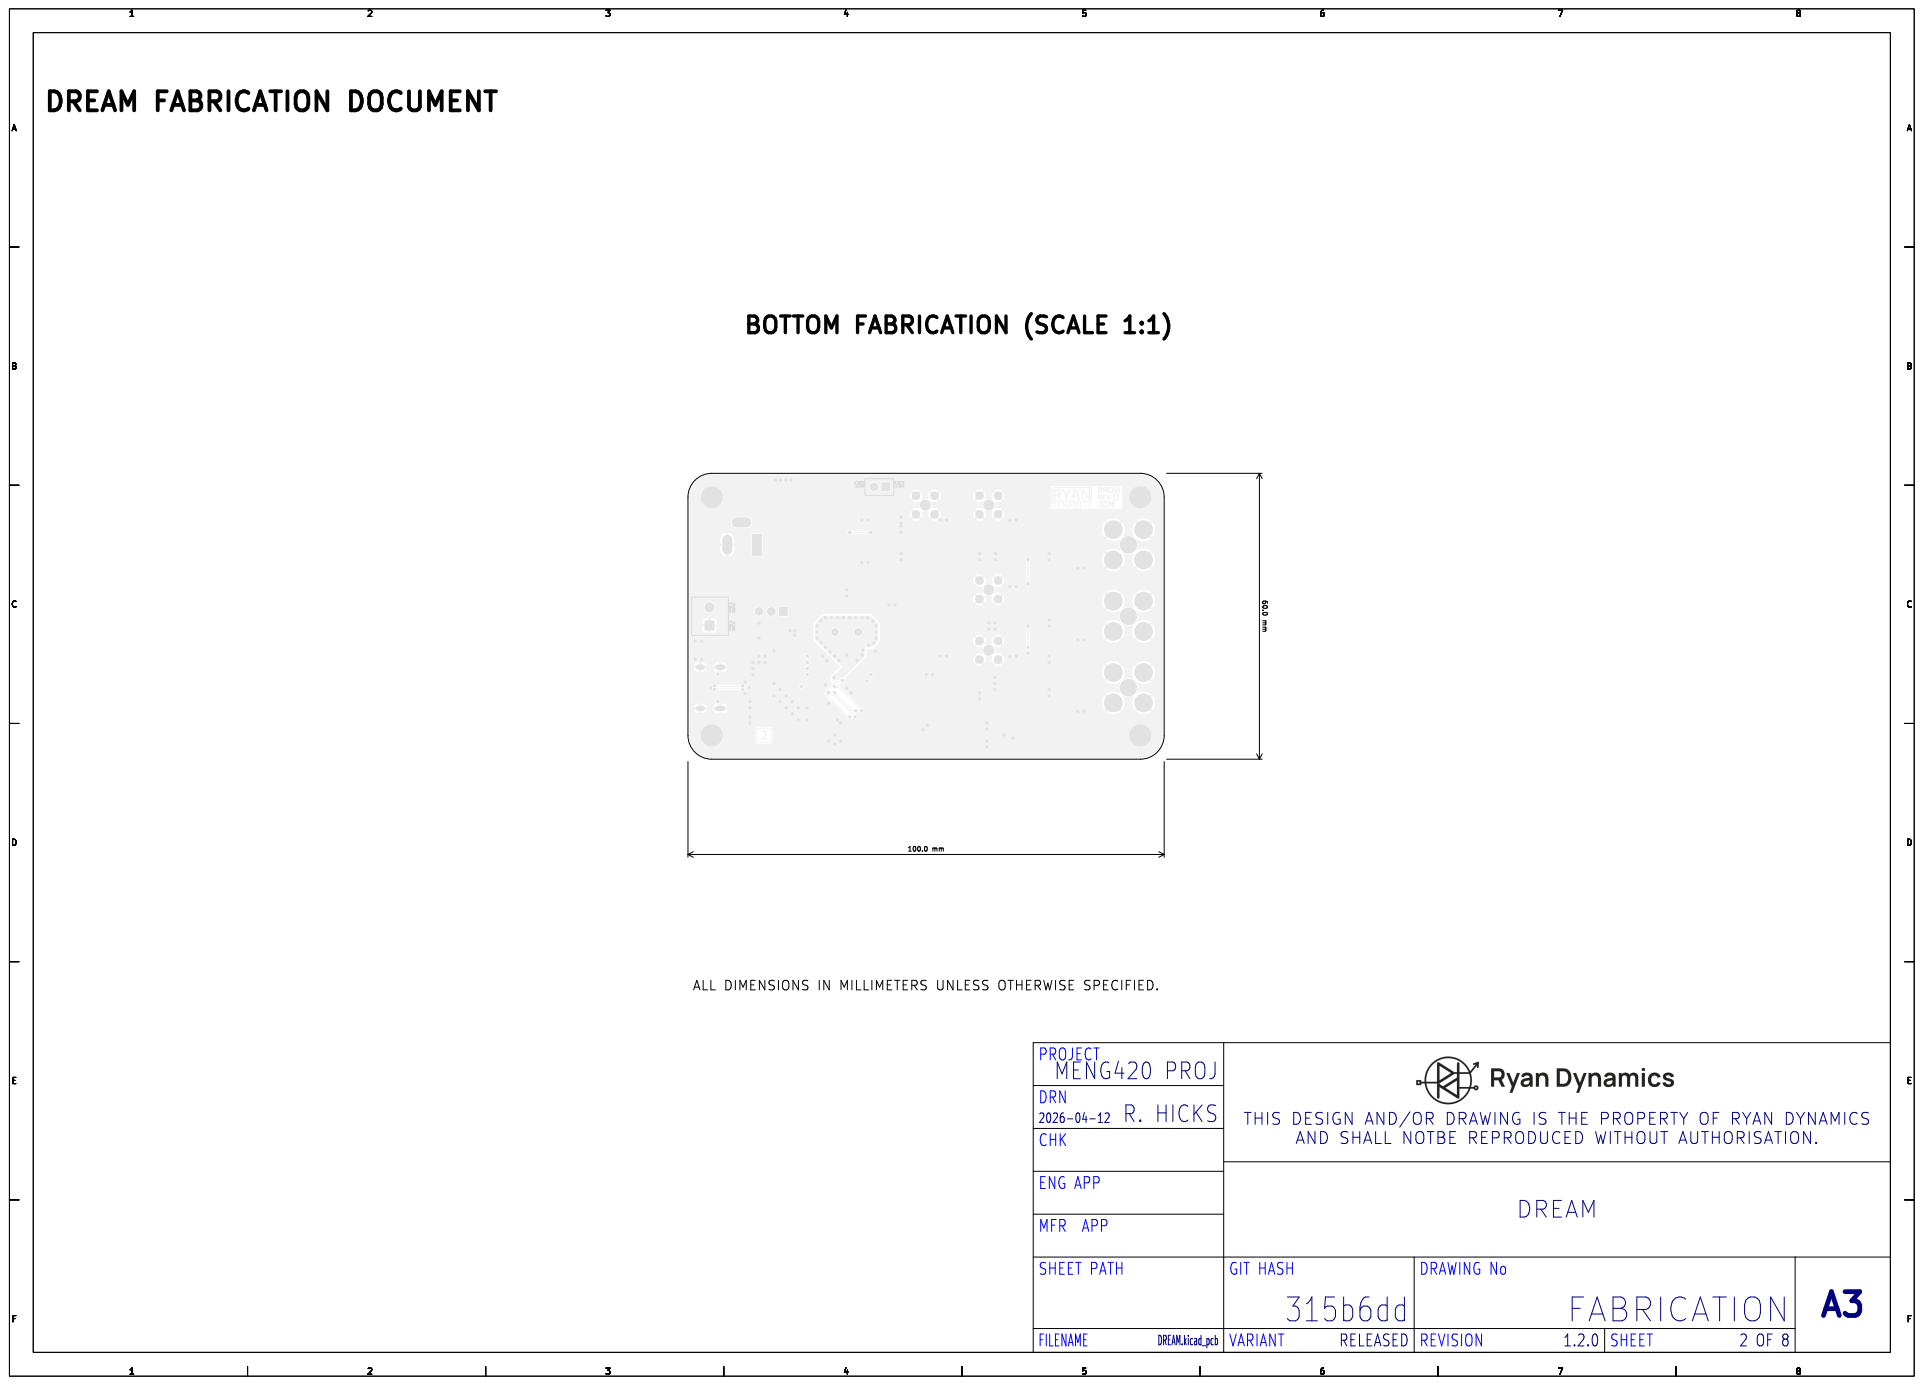
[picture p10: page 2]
DRAWING No; MENG420; PROJ; DREAM; ENG APP; GIT; HASH; SHEET; PATH; MFR; APP; R. HICKS; ALL; DIMENSIONS; MILLIMETERS; UNLESS OTHERWISE; SPECIFIED.; REV

PROJECT
DRN
THIS DESIGN AND/OR DRAWING IS THE PROPERTY OF RYAN DYNAMICSAND SHALL NOTBE REPRODUCED WITHOUT AUTHORISATION.
CHK

DRILL | DRAWING L1 - L2 (SCALE | 1:1)
DREAM | FABRICATION | DOCUMENT

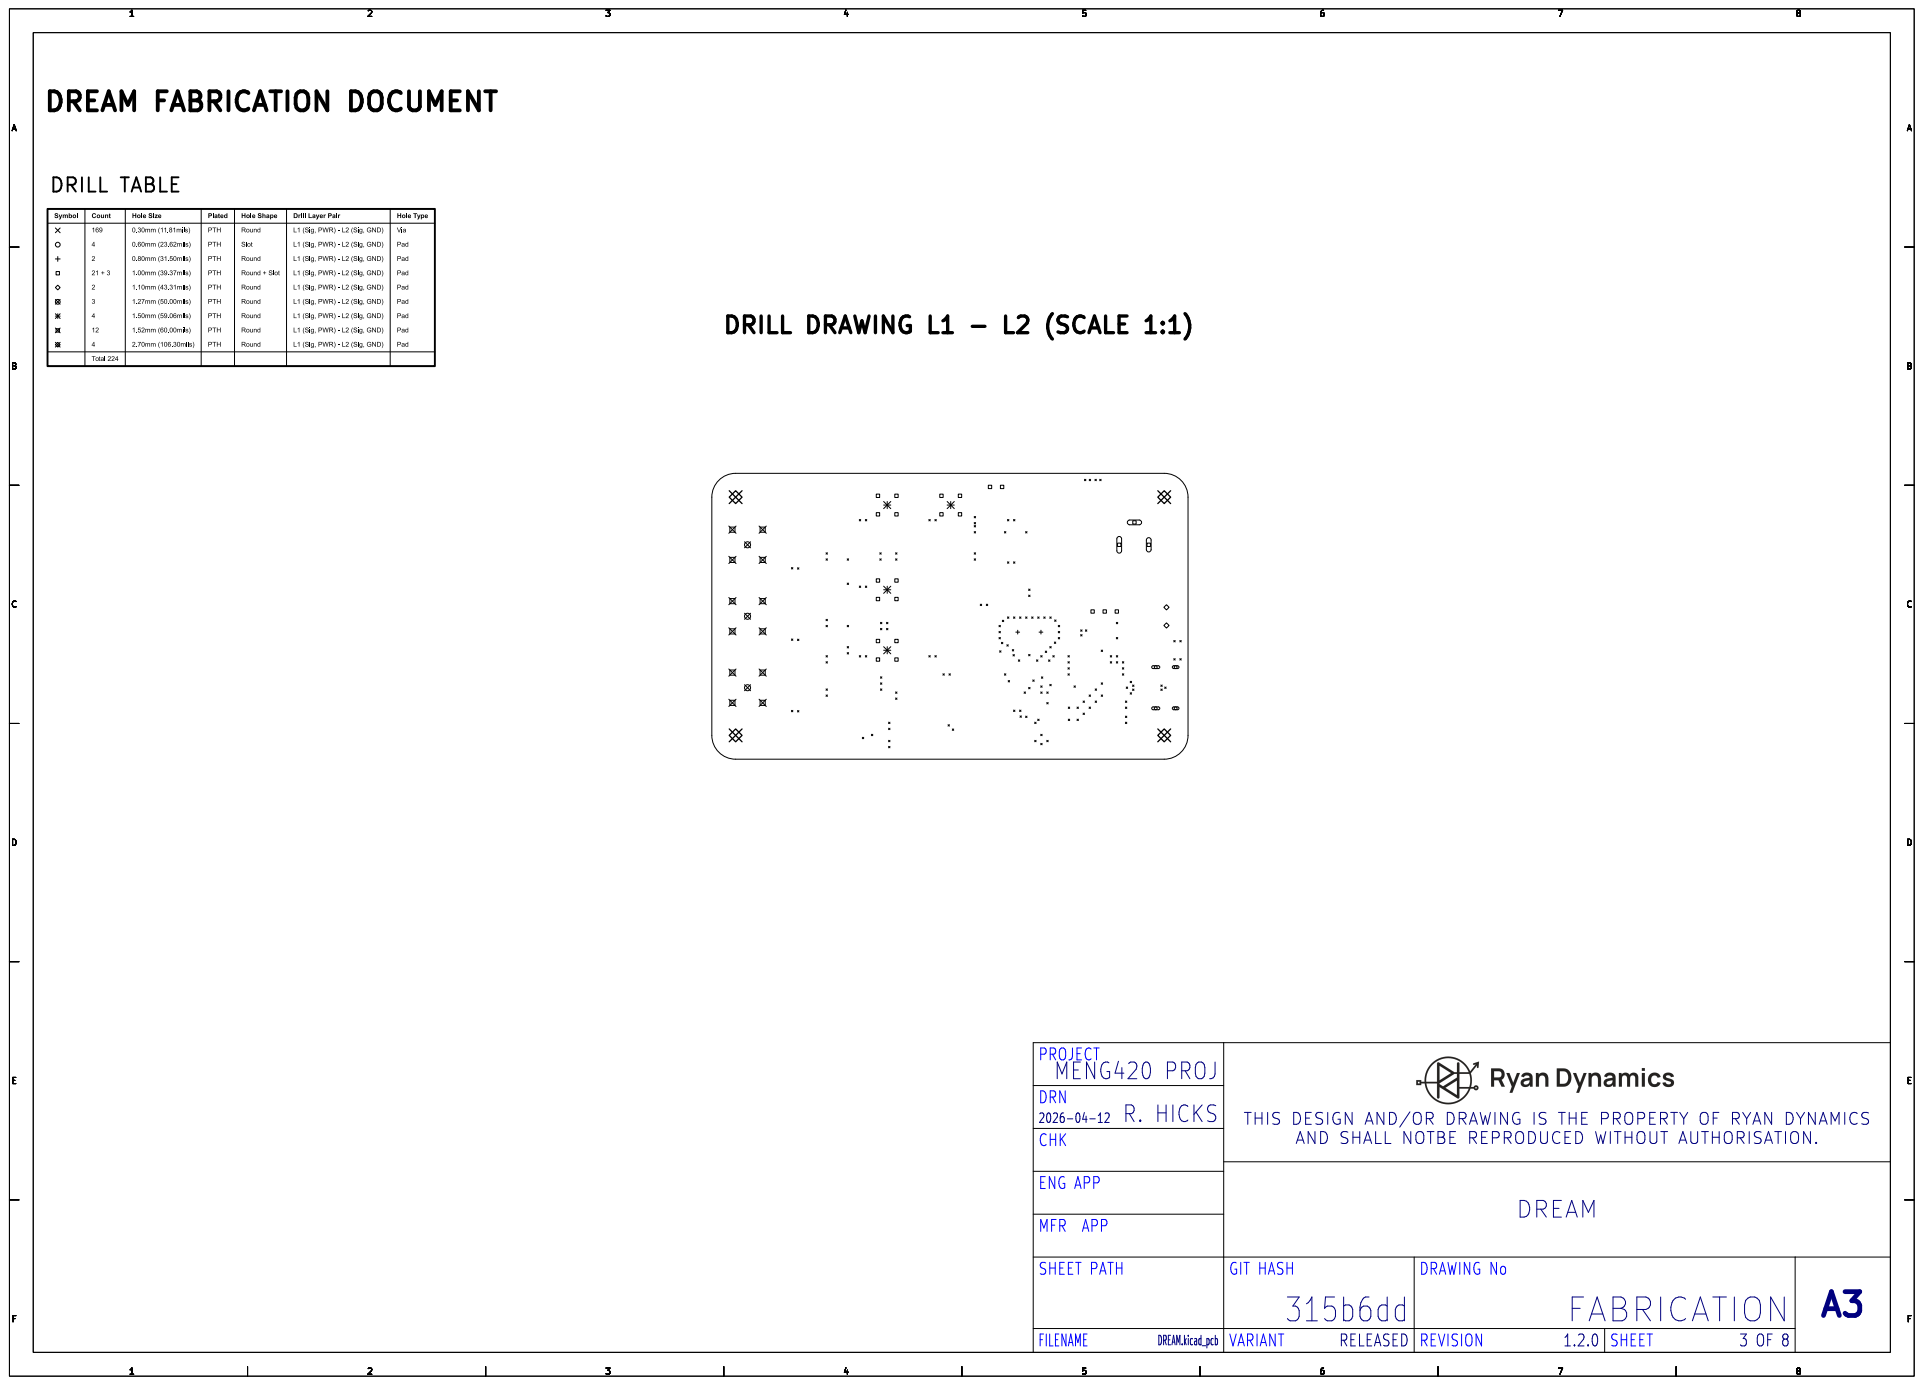
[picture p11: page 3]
DRAWING No; MENG420; PROJ; DREAM; ENG APP; GIT; HASH; SHEET; PATH; MFR; APP; R. HICKS; DRILL TABLE

PROJECT
DRN
THIS DESIGN AND/OR DRAWING IS THE PROPERTY OF RYAN DYNAMICSAND SHALL NOTBE REPRODUCED WITHOUT AUTHORISATION.
CHK

DRILL | DRAWING L1 - L2 (SCALE | 1:1)
DREAM | FABRICATION | DOCUMENT

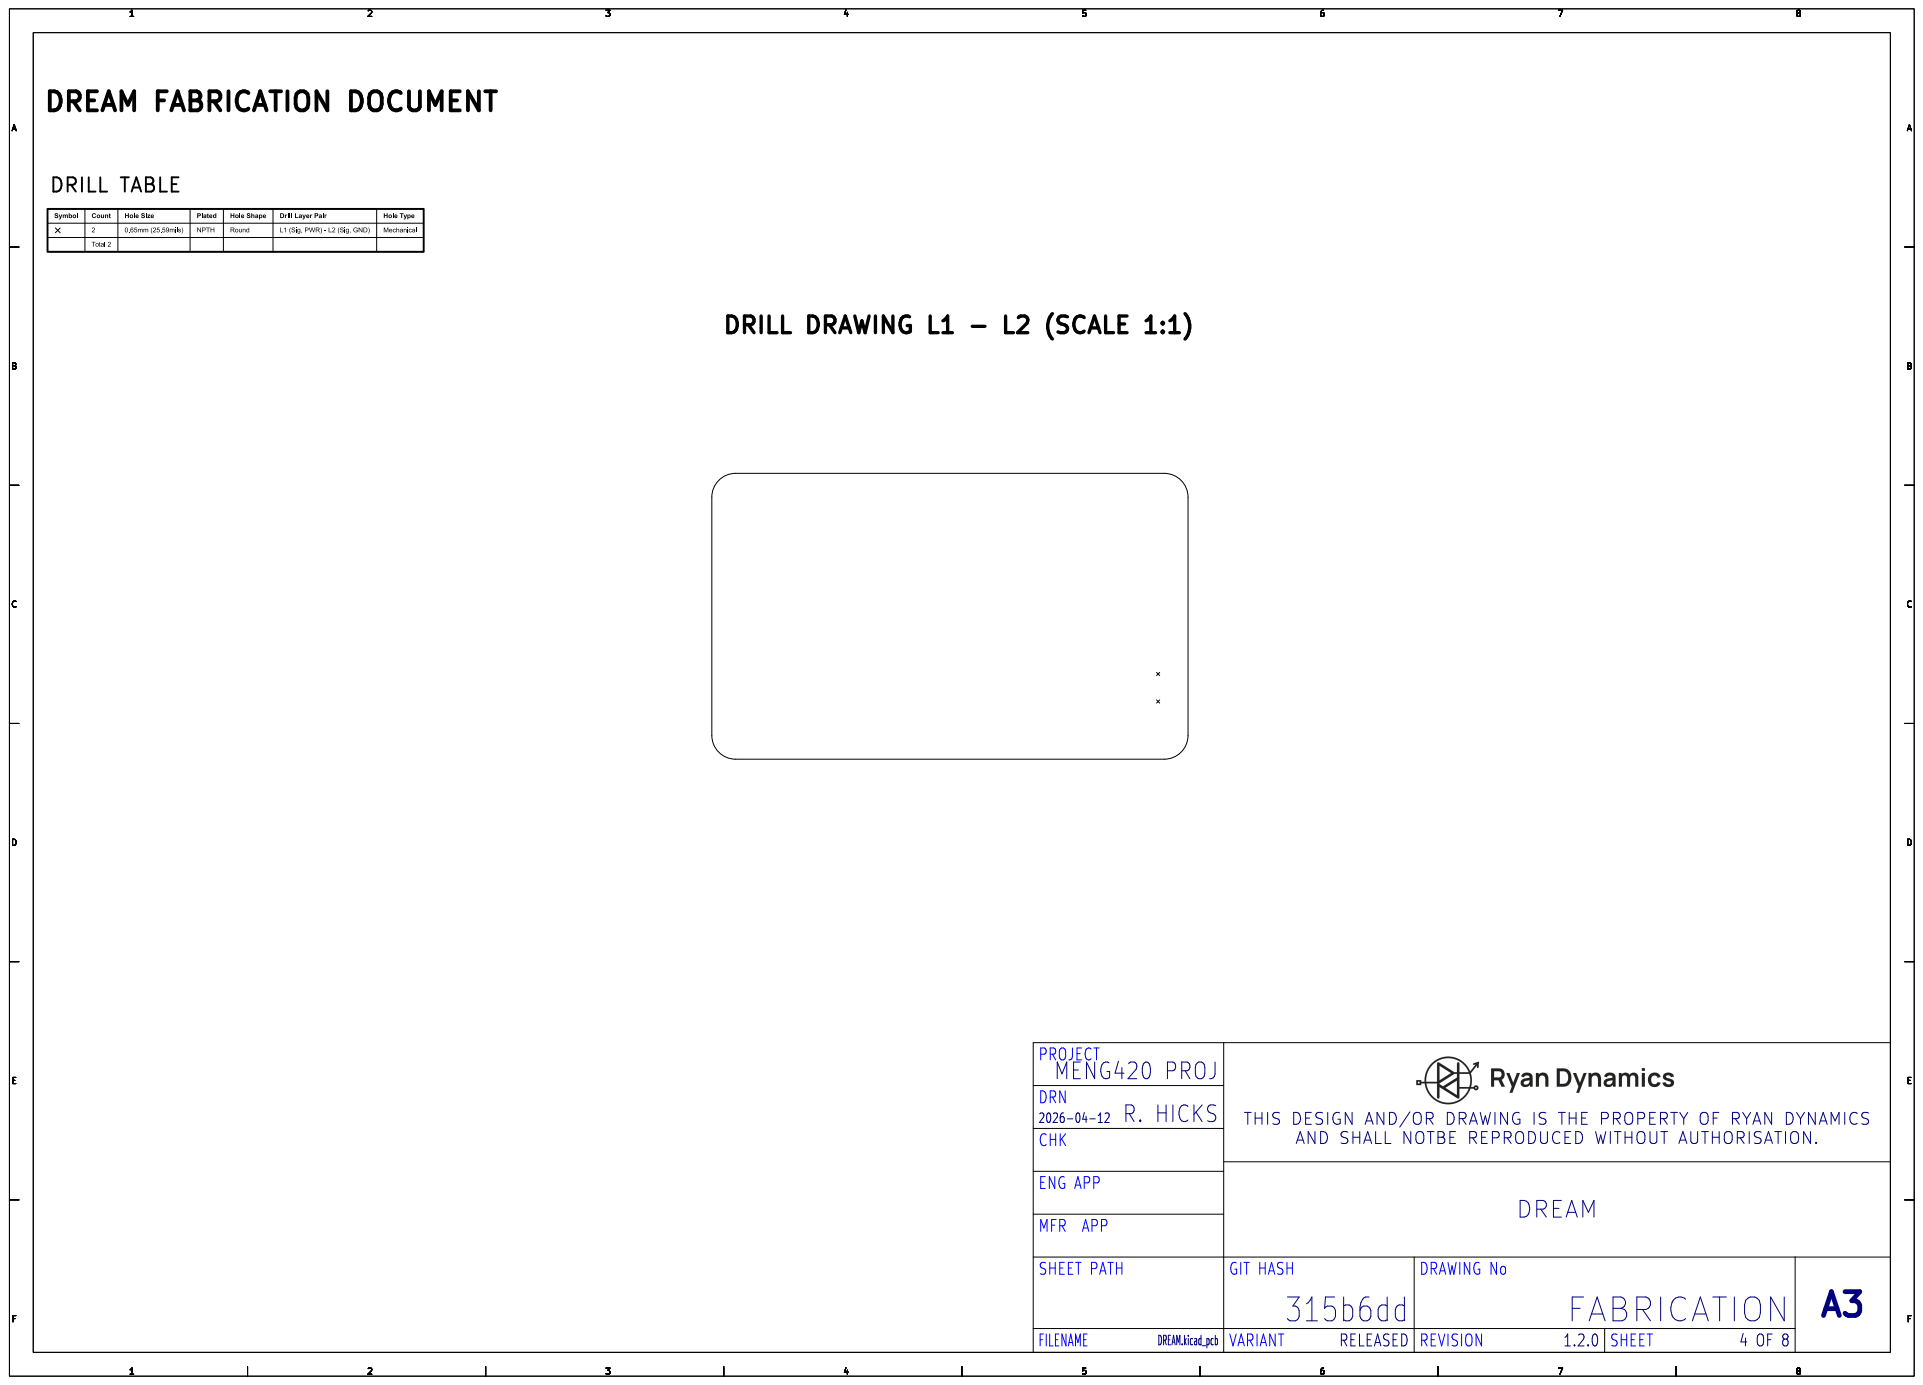
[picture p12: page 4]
DRAWING No; MENG420; PROJ; PROJECT; DREAM; ENG APP; 2026-04-12 CHK; GIT; HASH; SHEET; PATH; MFR; APP; DRN; R. HICKS; THIS DESIGN AND/OR; DRAWING IS THE PROPERTY OF RYAN DYNAMICSAND SHALL NOTBE REPRODUCED WITHOUT AUTHORISATION.; DRILL TABLE

# TOP TEST POINTS (SCALE 1:1)

# DREAM FABRICATION DOCUMENT

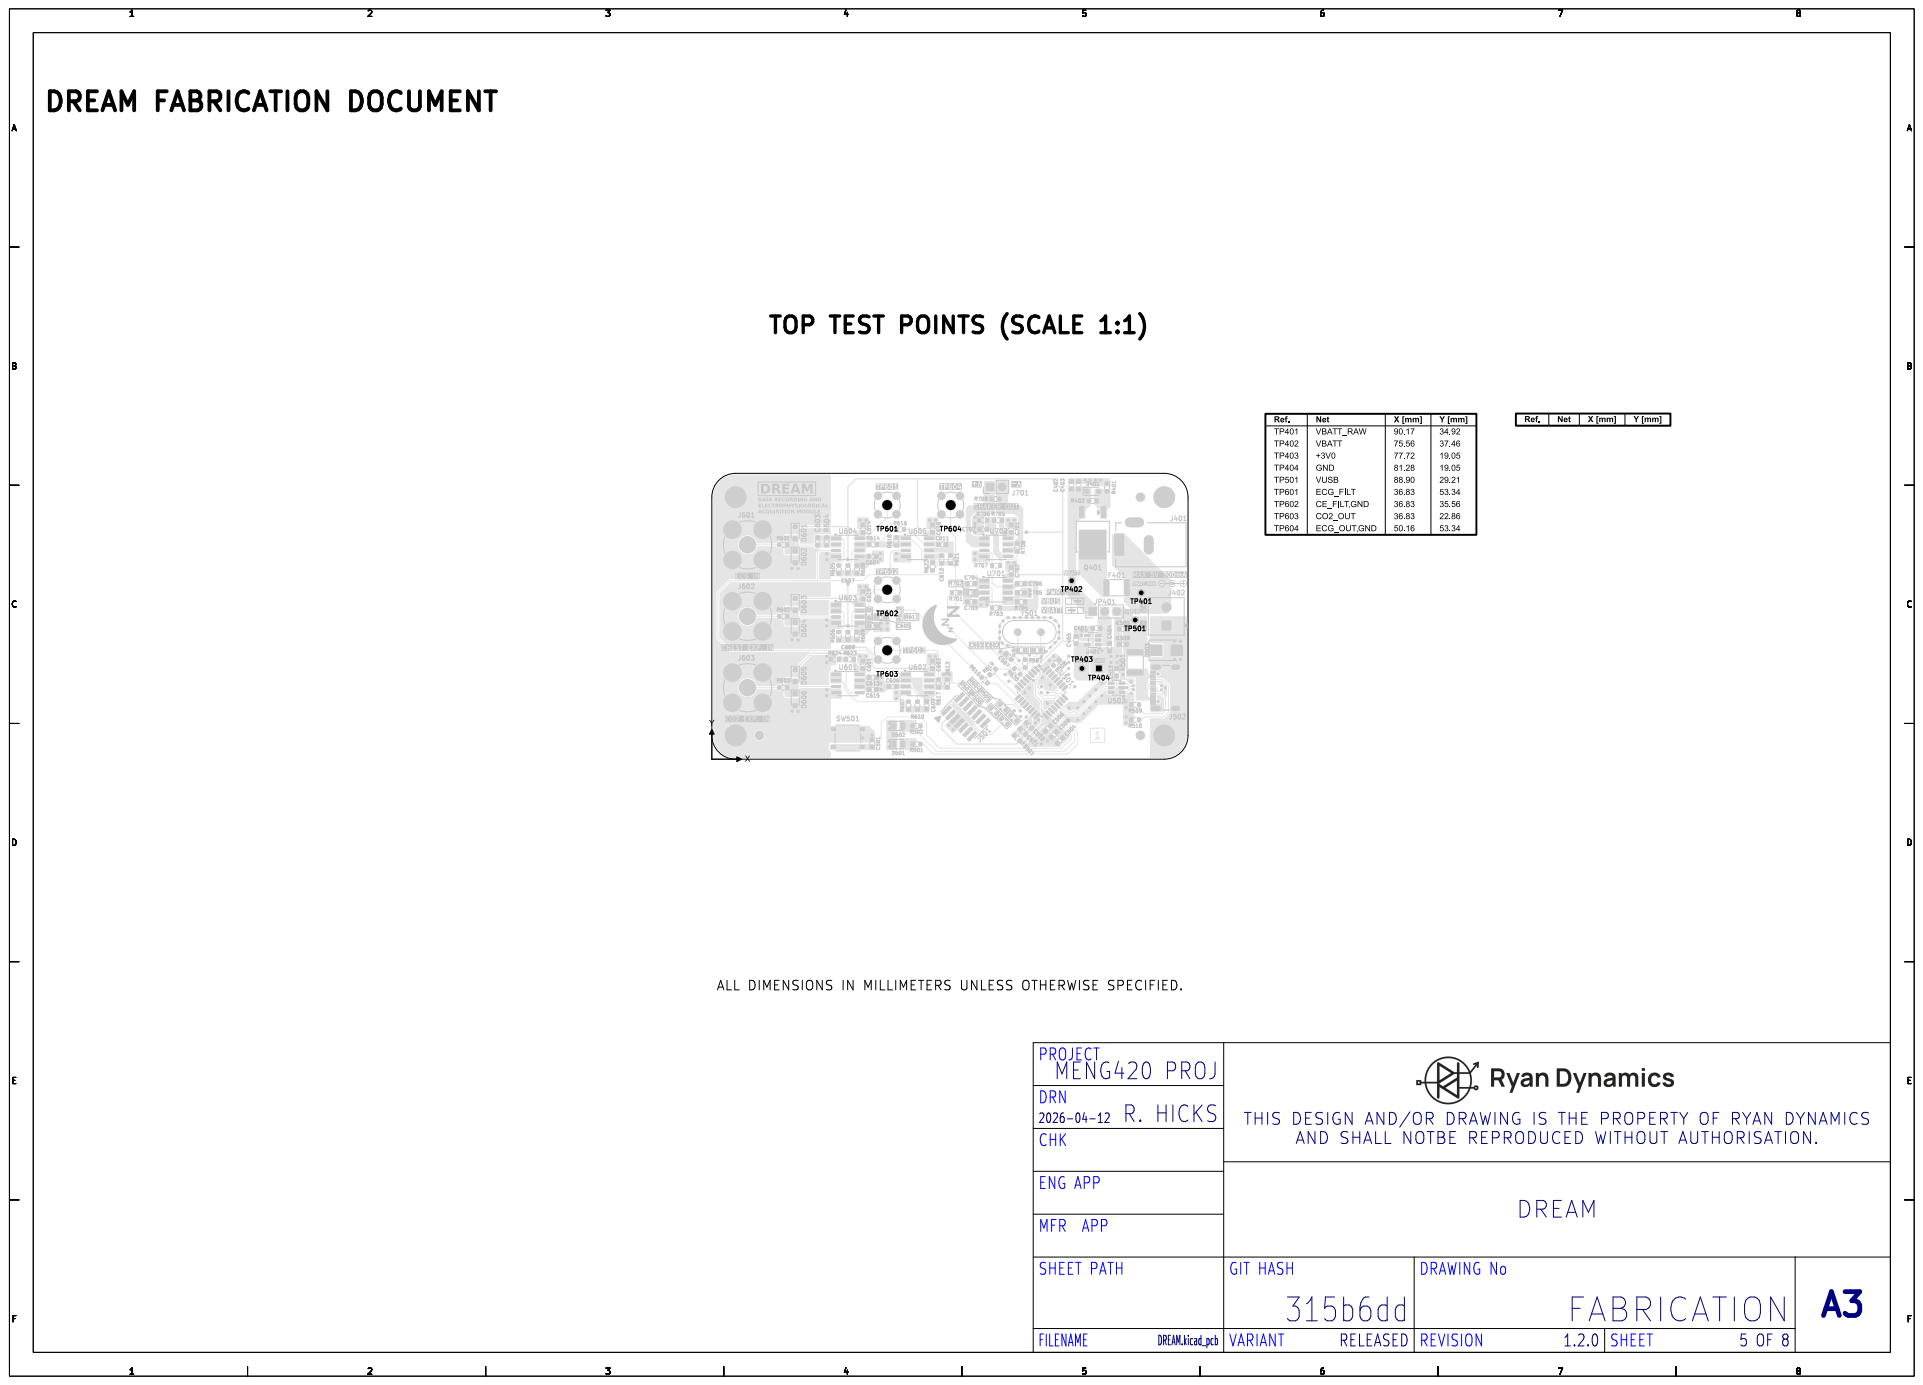
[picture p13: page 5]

ALL DIMENSIONS IN MILLIMETERS UNLESS OTHERWISE SPECIFIED.

PROJECT
MENG420 PROJ
DRN
THIS DESIGN AND/OR DRAWING IS THE PROPERTY OF RYAN DYNAMICSAND SHALL NOTBE REPRODUCED WITHOUT AUTHORISATION.
CHK

BOTTOM | TEST | POINTS (SCALE | 1:1)
DREAM | FABRICATION | DOCUMENT

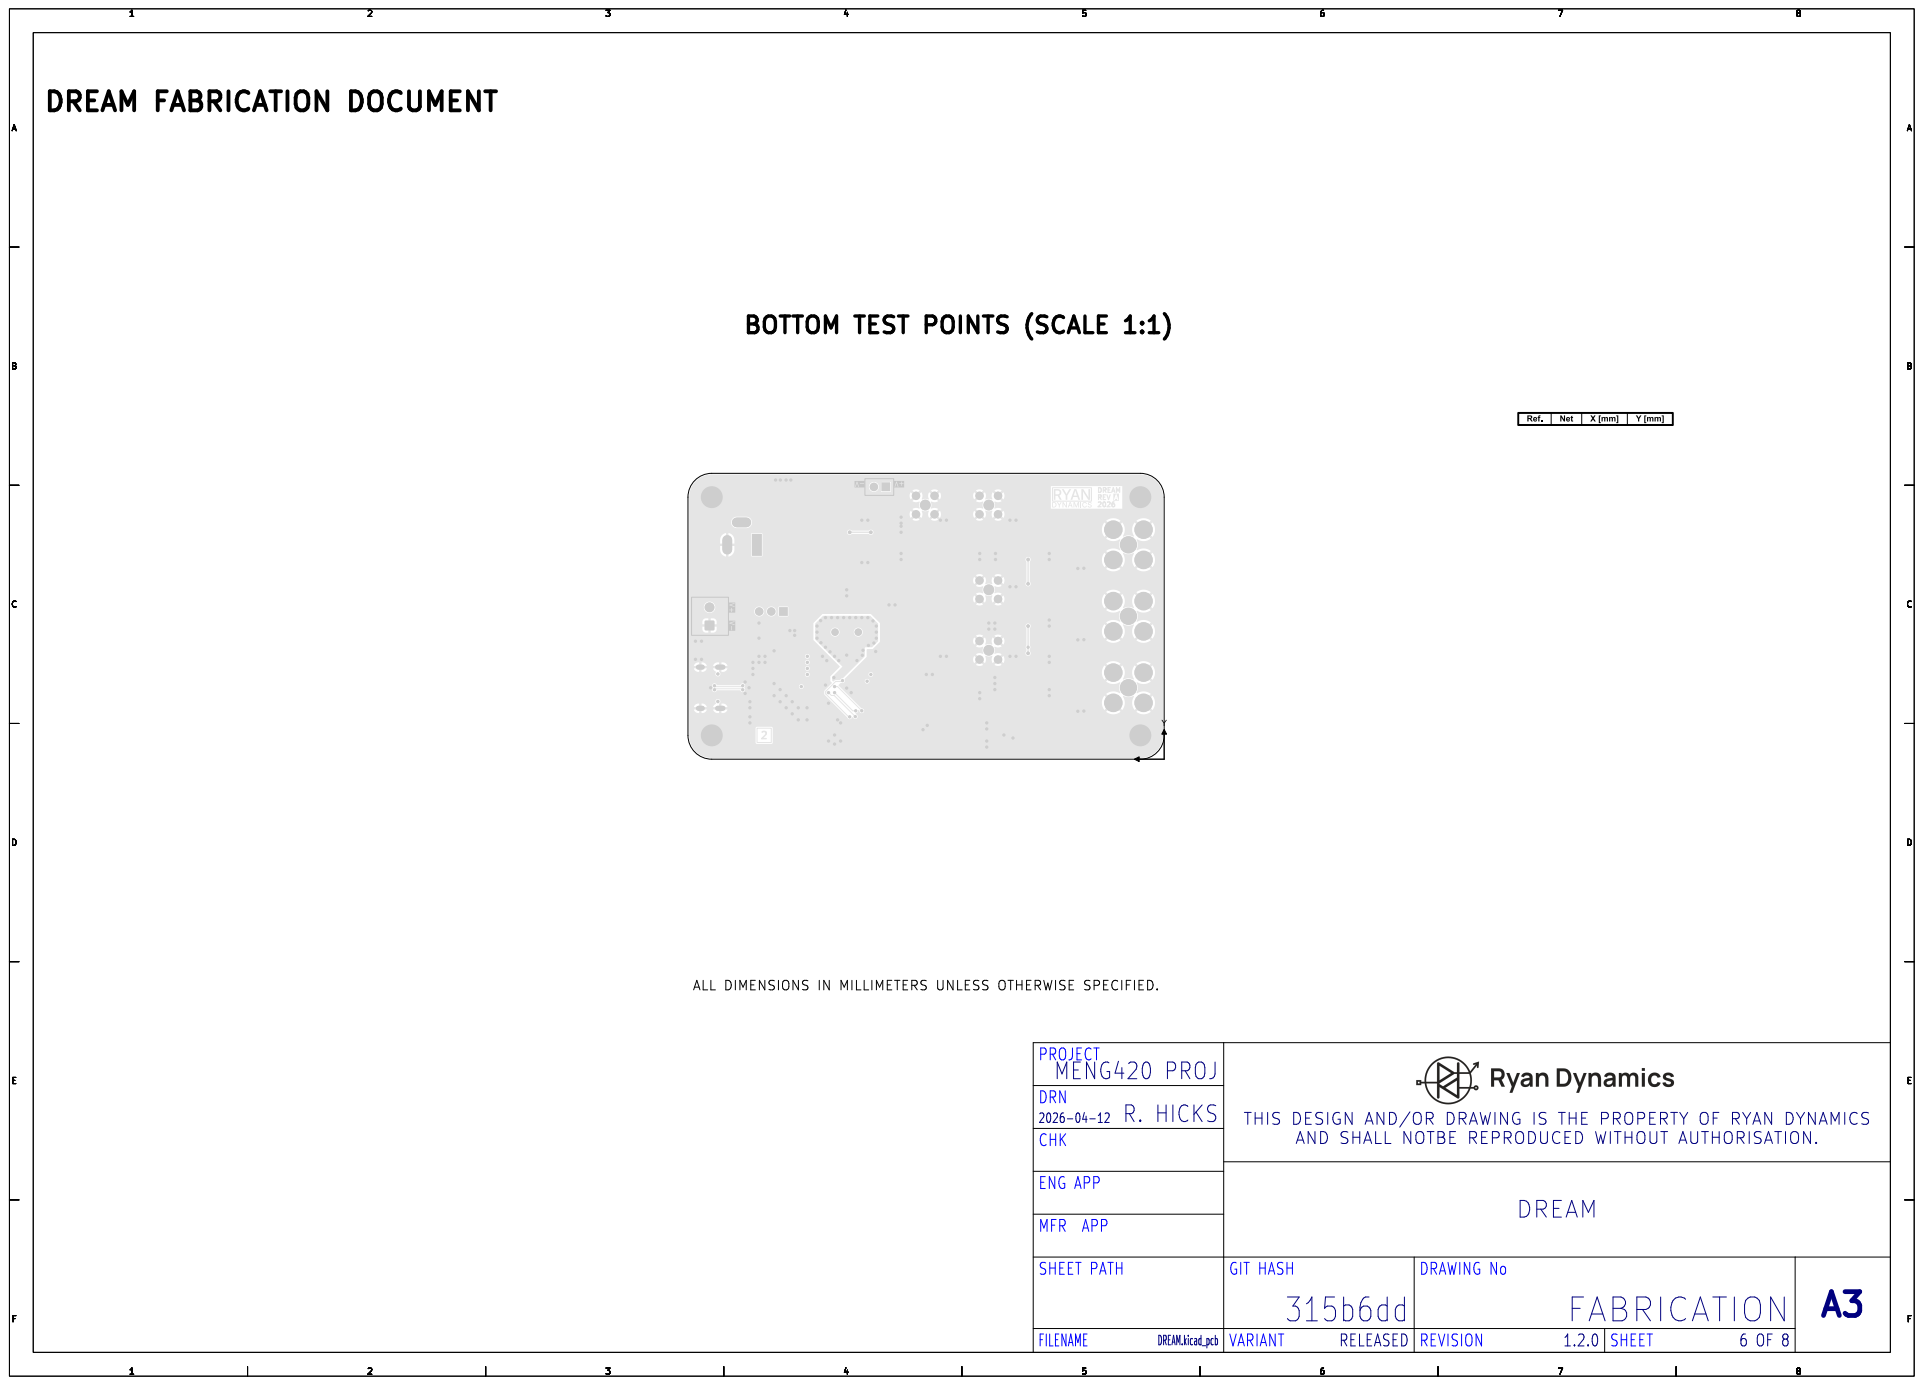
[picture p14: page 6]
DRAWING No; MENG420; PROJ; PROJECT; DREAM; ENG APP; 2026-04-12 CHK; GIT; HASH; SHEET; PATH; MFR; APP; DRN; R. HICKS; THIS DESIGN AND/OR; DRAWING IS THE PROPERTY OF RYAN DYNAMICSAND SHALL NOTBE REPRODUCED WITHOUT AUTHORISATION.; ALL; DIMENSIONS; MILLIMETERS; UNLESS OTHERWISE; SPECIFIED.; REV

L1 (Sig, | PWR) (SCALE 1:1)
DREAM | FABRICATION | DOCUMENT

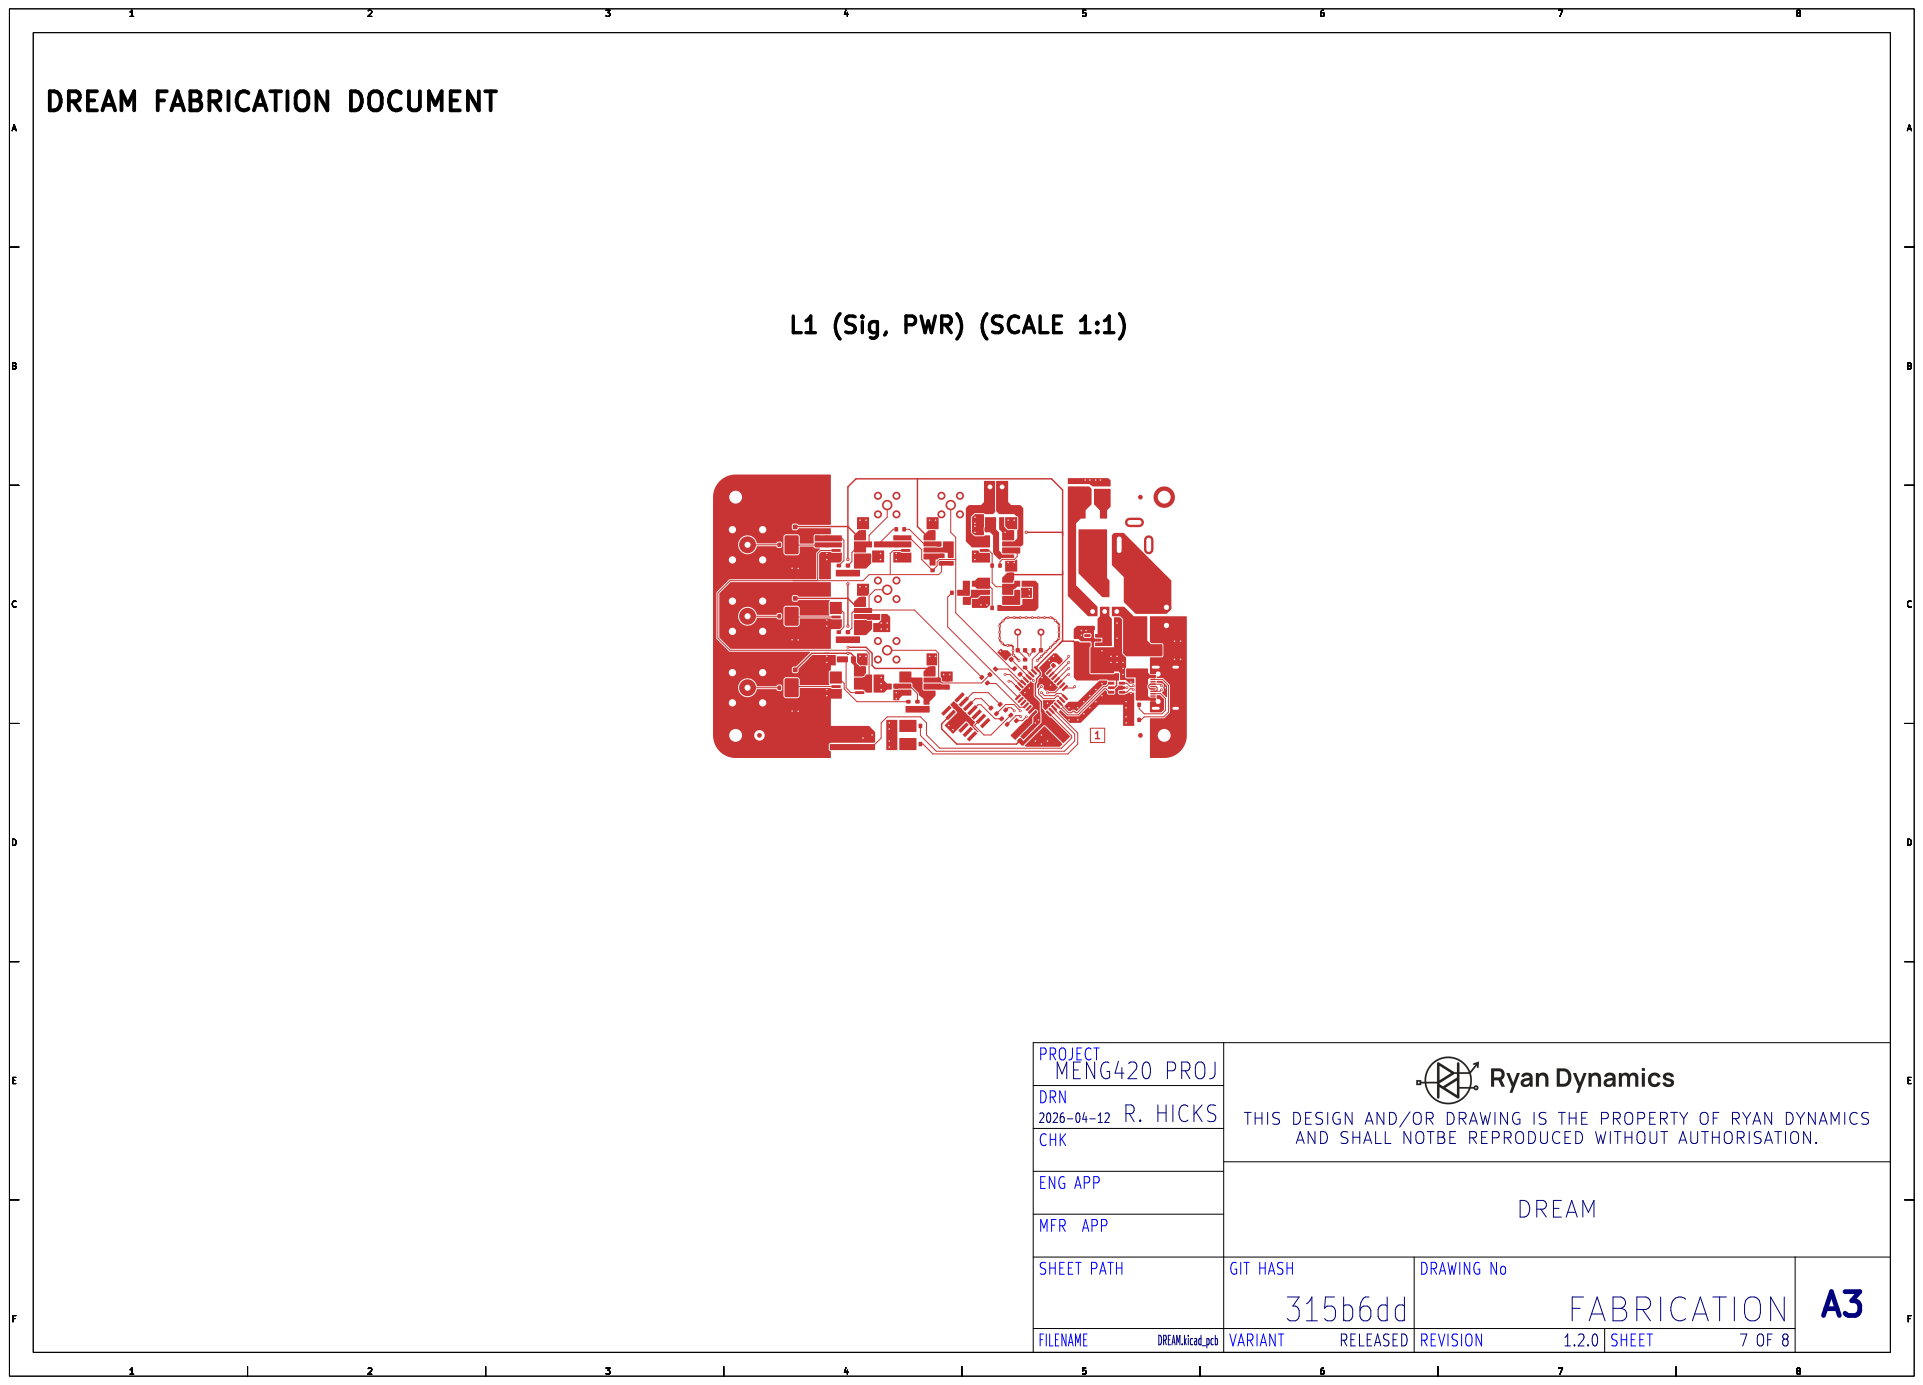
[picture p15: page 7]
DRAWING No; MENG420; PROJ; PROJECT; DREAM; ENG APP; 2026-04-12 CHK; GIT; HASH; SHEET; PATH; MFR; APP; DRN; R. HICKS; THIS DESIGN AND/OR; DRAWING IS THE PROPERTY OF RYAN DYNAMICSAND SHALL NOTBE REPRODUCED WITHOUT AUTHORISATION.

# L2 (Sig, GND) (SCALE 1:1)

DREAM | FABRICATION | DOCUMENT

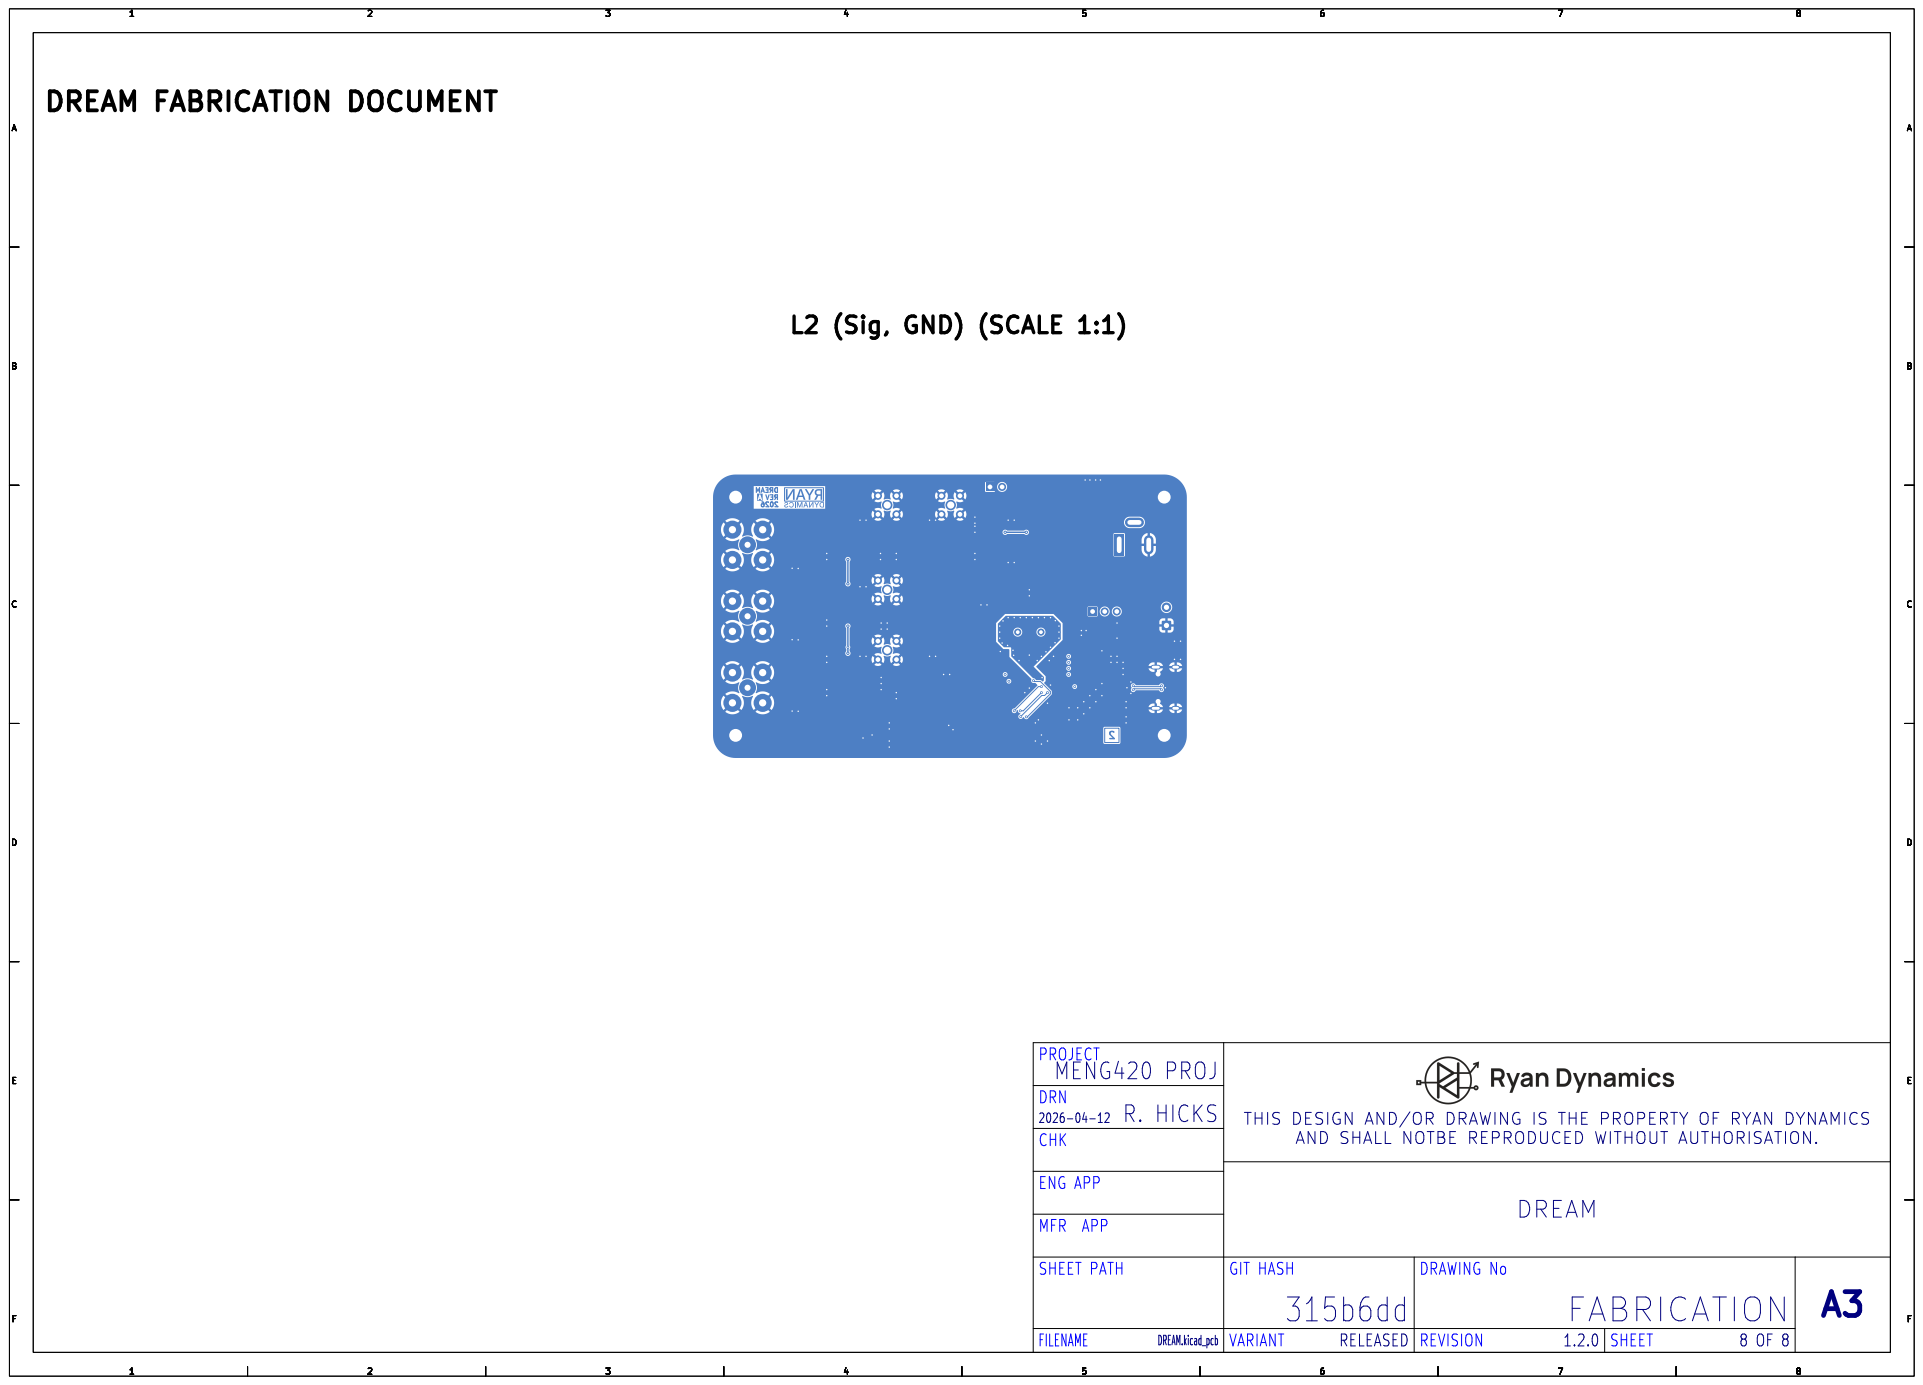
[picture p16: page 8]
DRAWING No; MENG420; PROJ; PROJECT; DREAM; ENG APP; 2026-04-12 CHK; GIT; HASH; SHEET; PATH; MFR; APP; DRN; R. HICKS; THIS DESIGN AND/OR; DRAWING IS THE PROPERTY OF RYAN DYNAMICSAND SHALL NOTBE REPRODUCED WITHOUT AUTHORISATION.; REV

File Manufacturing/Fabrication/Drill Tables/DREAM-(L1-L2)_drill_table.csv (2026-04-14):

Count | Hole Size | Plated | Hole Shape | Drill Layer Pair | Hole Type
169 | 0.30mm (11.81mils) | PTH | Round | L1 (Sig, PWR) - L2 (Sig, GND) | Via
4 | 0.60mm (23.62mils) | PTH | Slot | L1 (Sig, PWR) - L2 (Sig, GND) | Pad
2 | 0.80mm (31.50mils) | PTH | Round | L1 (Sig, PWR) - L2 (Sig, GND) | Pad
21 + 3 | 1.00mm (39.37mils) | PTH | Round + Slot | L1 (Sig, PWR) - L2 (Sig, GND) | Pad
2 | 1.10mm (43.31mils) | PTH | Round | L1 (Sig, PWR) - L2 (Sig, GND) | Pad
3 | 1.27mm (50.00mils) | PTH | Round | L1 (Sig, PWR) - L2 (Sig, GND) | Pad
4 | 1.50mm (59.06mils) | PTH | Round | L1 (Sig, PWR) - L2 (Sig, GND) | Pad
12 | 1.52mm (60.00mils) | PTH | Round | L1 (Sig, PWR) - L2 (Sig, GND) | Pad
4 | 2.70mm (106.30mils) | PTH | Round | L1 (Sig, PWR) - L2 (Sig, GND) | Pad
Total 224

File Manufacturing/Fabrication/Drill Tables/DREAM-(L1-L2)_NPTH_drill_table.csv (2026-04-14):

Count | Hole Size | Plated | Hole Shape | Drill Layer Pair | Hole Type
2 | 0.65mm (25.59mils) | NPTH | Round | L1 (Sig, PWR) - L2 (Sig, GND) | Mechanical
Total 2

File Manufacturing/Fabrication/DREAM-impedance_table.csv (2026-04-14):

Transmission Line | Impedance [ohms] | Tolerance [ohms] | Layer | Trace Width [mm] | Gap [mm] | Ref. Layers

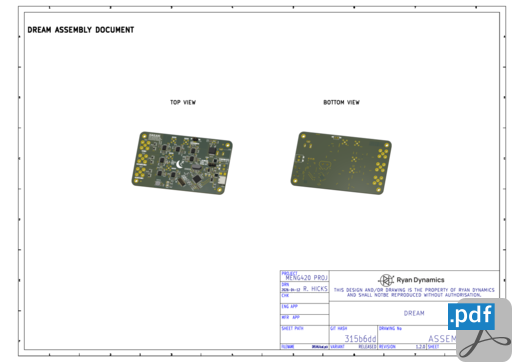
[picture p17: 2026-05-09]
HTML/images/cat_pdf_assembly_DREAM-assembly.png

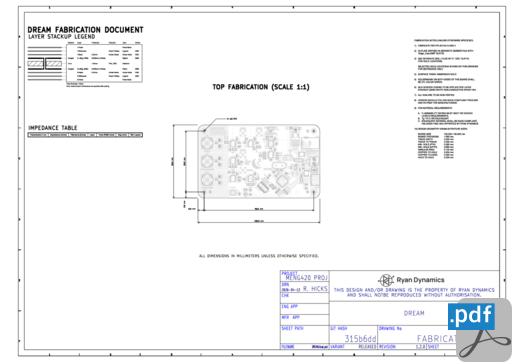
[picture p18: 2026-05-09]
HTML/images/cat_pdf_fabrication_DREAM-fabrication.png

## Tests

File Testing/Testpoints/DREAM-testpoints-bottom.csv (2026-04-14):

Ref. | Net | X [mm] | Y [mm]

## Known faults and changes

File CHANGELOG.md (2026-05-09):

# Changelog

## [Unreleased]

## [1.2.0] - 2026-05-09

### Added

-   Added 3D models to some footprints missing them

### Fixed

-   Changed gain of ECG chain to x10 from x24.9
-   Compiled entire schematic into single sheet

## [1.1.0] - 2026-04-14

### Fixed

-   Add ground pour underneath uC

## [1.0.3] - 2026-04-14

### Changed

-   Crystal oscillator layout, isolated ground pour, ground perimeter

## [1.0.2] - 2026-04-14

### Added

-   Added some silkscreen flair
-   Broke out unused STM32 pins to vias
-   Added pin 1 indicator to JTAG header

### Fixed

-   Changed VBUS_RAW to VBUS
-   Changed VBUS to VUSB

## [1.0.1] - 2026-04-14

### Added

-   Ground pour underneath XTAL.
-   Untented via flag set
-   Production files

## [1.0.0] - 2026-04-14

### Added

-   Schematic capture
-   Preliminary PCB layout

[Unreleased]: https://github.com/Reemuson/MENG4210-Project/compare/1.2.0...HEAD

[1.2.0]: https://github.com/Reemuson/MENG4210-Project/compare/1.1.0...1.2.0

[1.1.0]: https://github.com/Reemuson/MENG4210-Project/compare/1.0.3...1.1.0

[1.0.3]: https://github.com/Reemuson/MENG4210-Project/compare/1.0.2...1.0.3

[1.0.2]: https://github.com/Reemuson/MENG4210-Project/compare/1.0.1...1.0.2

[1.0.1]: https://github.com/Reemuson/MENG4210-Project/compare/1.0.0...1.0.1

[1.0.0]: https://github.com/Reemuson/MENG4210-Project/compare/ce0e9945835311aa06857bbd56dea8228dd248e1...1.0.0

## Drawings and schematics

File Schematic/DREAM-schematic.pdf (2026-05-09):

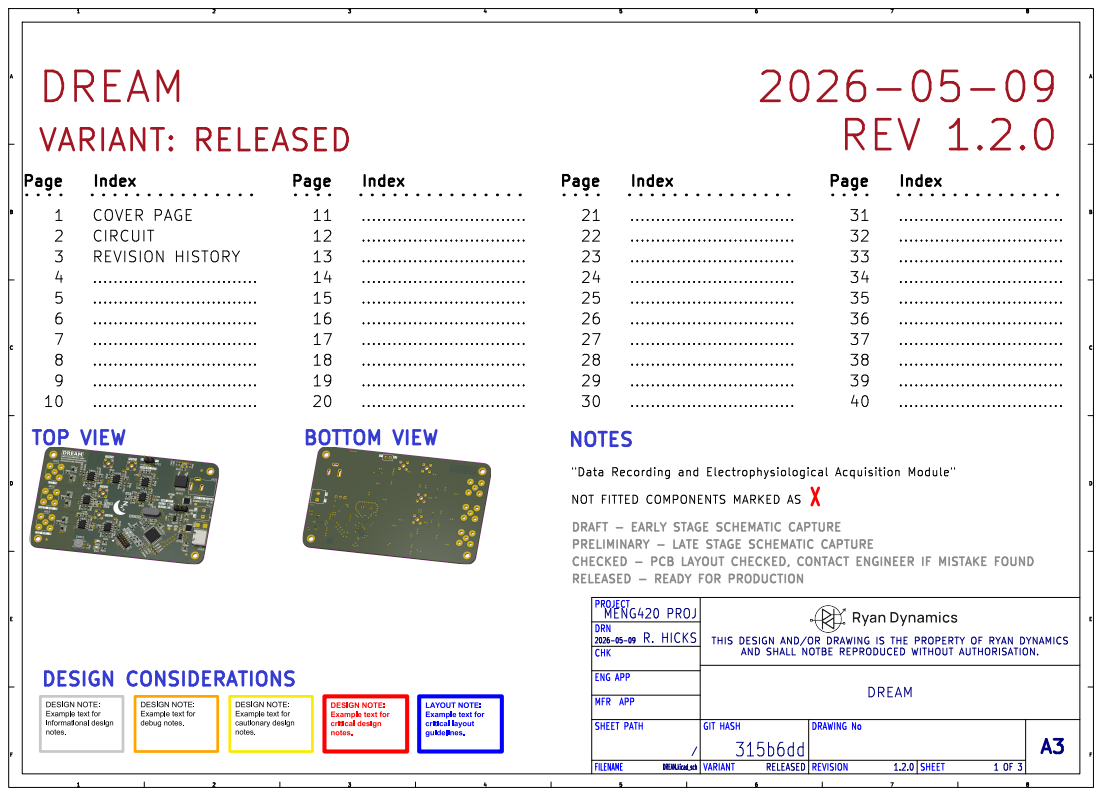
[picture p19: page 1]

NOT FITTED COMPONENTS MARKED AS

DRAFT - EARLY STAGE SCHEMATIC CAPTURE
PRELIMINARY - LATE STAGE SCHEMATIC CAPTURE
CHECKED - PCB LAYOUT CHECKED, CONTACT ENGINEER IF MISTAKE FOUND
RELEASED - READY FOR PRODUCTION

THIS DESIGN AND/OR DRAWING IS THE PROPERTY OF RYAN DYNAMICS

AND SHALL NOTBE REPRODUCED WITHOUT AUTHORISATION.

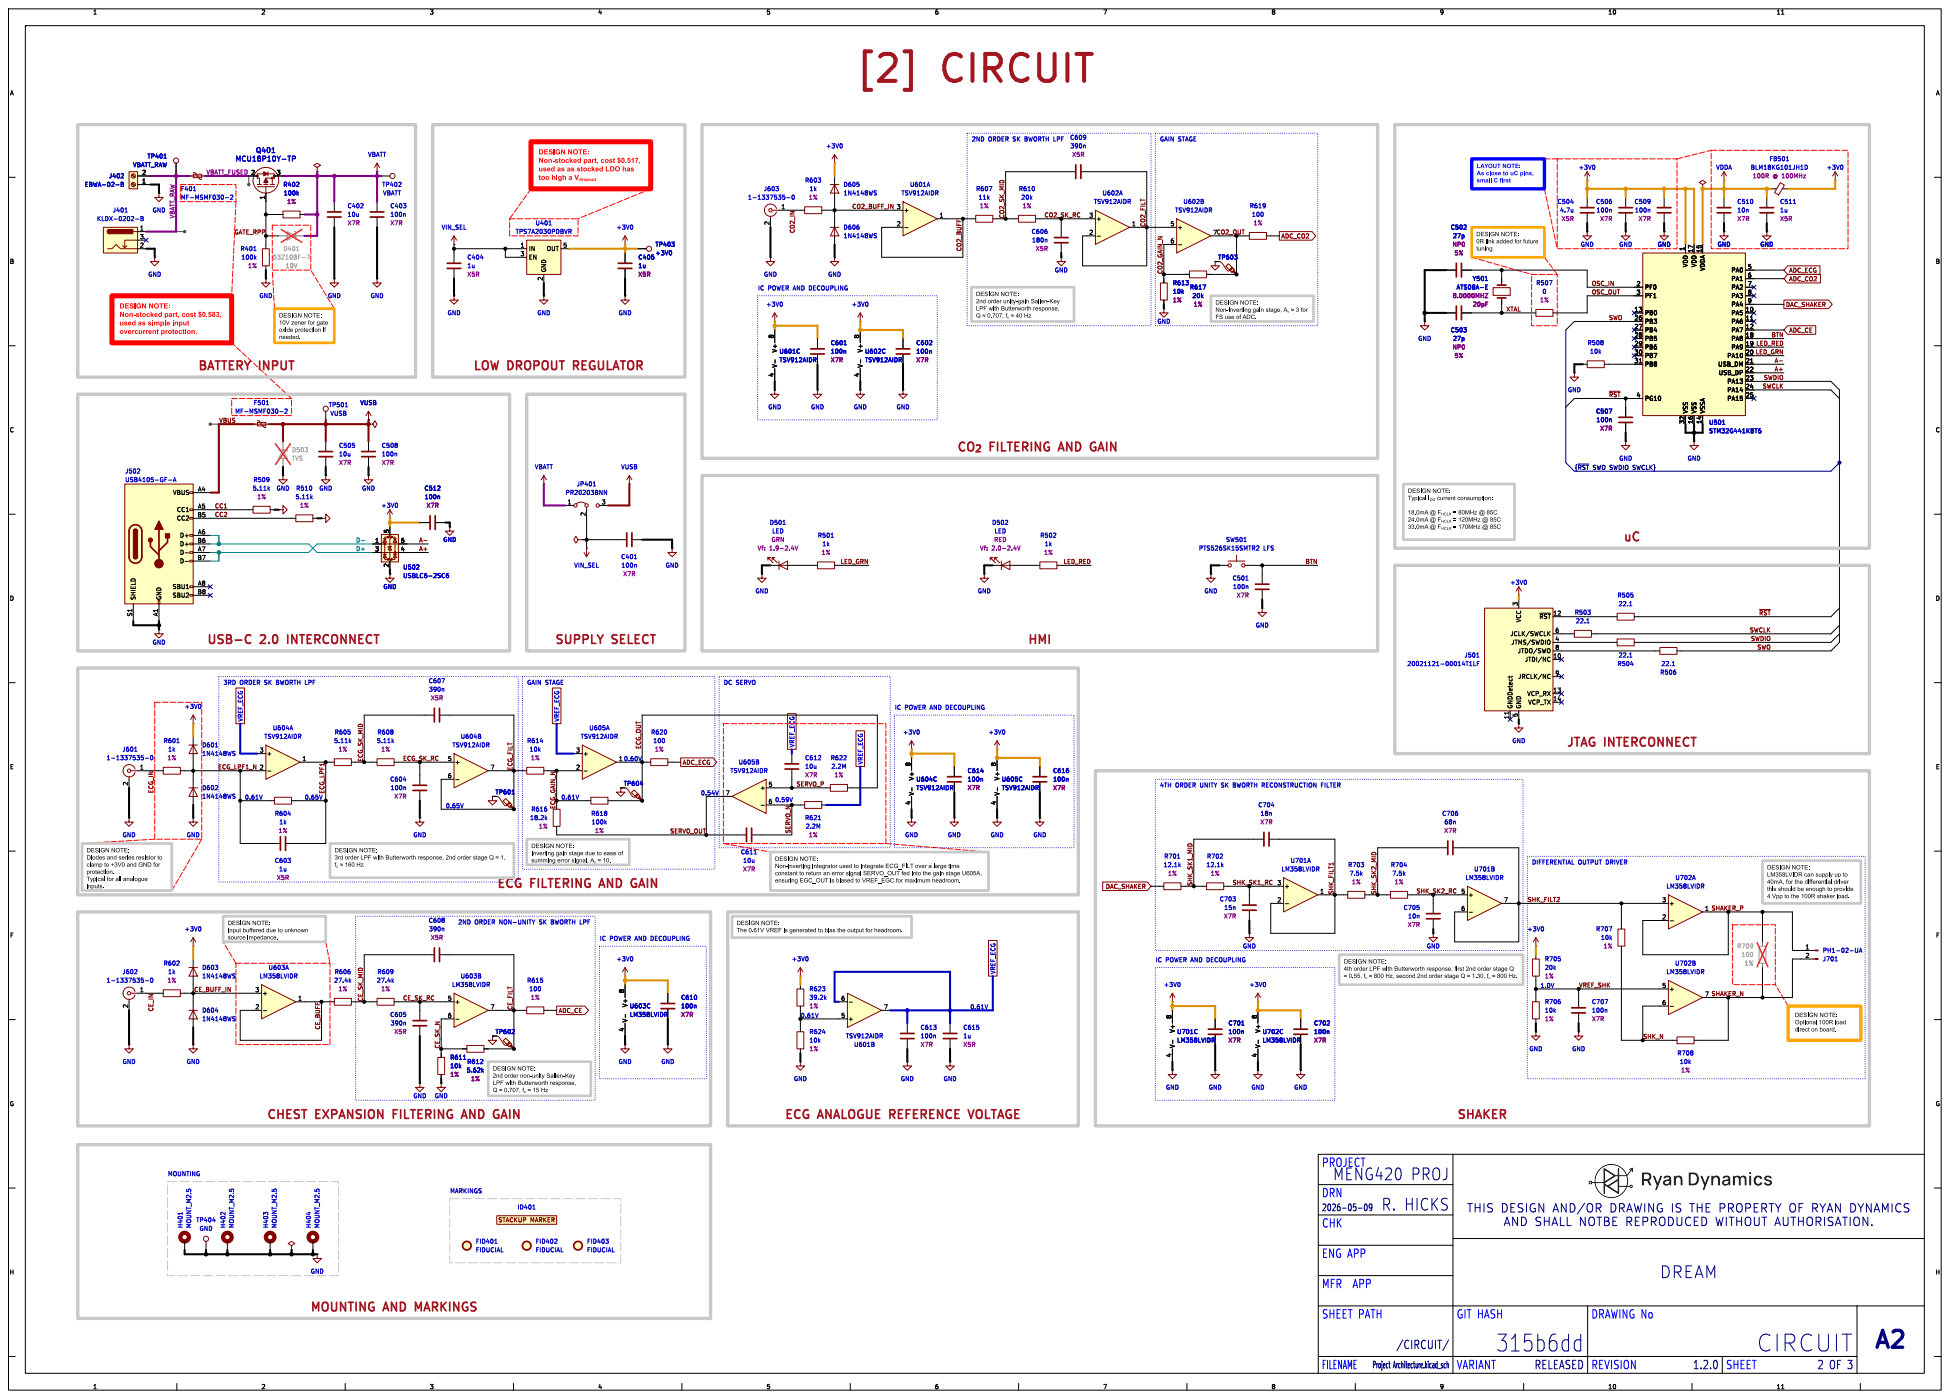
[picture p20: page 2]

DESIGN NOTE: 2nd order unity-gain Sallen-Key LPF with Butterworth response, Q þÿ"H0.707, f_{c} þÿ"H40 Hz [2] CIRCUIT

2ND ORDER SK BWORTH LPF

DESIGN NOTE: Non-stocked part, cost $0.517, used as as stocked LDO has

LAYOUT NOTE: As close to uC pins, small C first

DESIGN NOTE: 0R link added for future

1 VSS 32 VDD 17 VSS 16 VDDA 15 VSSA 14 PA0

IC POWER AND DECOUPLING

DESIGN NOTE: Non-stocked part, cost $0.583, used as simple input overcurrent protection.

DESIGN NOTE: Non-inverting gain stage, A_{v} þÿ"H3 for FS use of ADC. ECG ANALOGUE REFERENCE VOLTAGE

Inverting gain stage due to ease of summing error signal, A_{v} þÿ"H10. BATTERY INPUT

þÿ"H0.55, f_{c} þÿ"H800 Hz, second 2nd order stage Q þÿ"H1.30, f_{c} þÿ"H800 Hz. CO_{2}FILTERING AND GAIN

DESIGN NOTE: Typical I_{DD} current consumption: 18.0mA @ F_{HCLK} = 80MHz @ 85C

3RD ORDER SK BWORTH LPF

4TH ORDER UNITY SK BWORTH RECONSTRUCTION FILTER

DESIGN NOTE: Diodes and series resistor to

DESIGN NOTE: 3rd order LPF with Butterworth response, 2nd order stage Q þÿ"H1,

direct on board. DESIGN NOTE:

DESIGN NOTE: Non-inverting integrator used to integrate ECG_FILT over a large time

clamp to +3V0 and GND for protection.

DESIGN NOTE: LM358LVIDR can supply up to

Typical for all analogue
inputs.

ECG FILTERING AND GAIN

constant to return an error signal SERVO_OUT fed into the gain stage U605A, ensuring EGC_OUT is biased to VREF_EGC for maximum headroom.

40mA, for the differential driver
this should be enough to provide
4 Vpp to the 100R shaker load.

DESIGN NOTE:
Input buffered due to unknown
source impedance.

2ND ORDER NON-UNITY SK BWORTH LPF

DESIGN NOTE: 4th order LPF with Butterworth response, first 2nd order stage Q

DESIGN NOTE: Optional 100R load

CHEST EXPANSION FILTERING AND GAIN

THIS DESIGN AND/OR DRAWING IS THE PROPERTY OF RYAN DYNAMICS

AND SHALL NOTBE REPRODUCED WITHOUT AUTHORISATION.

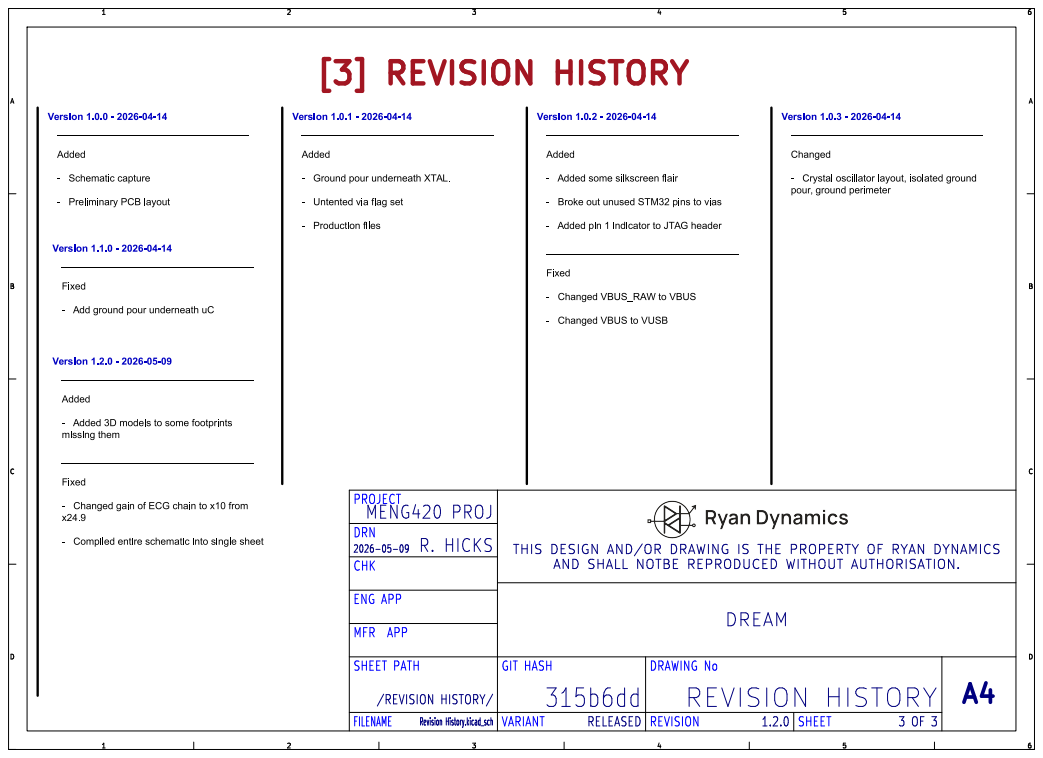
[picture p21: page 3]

- Ground pour underneath XTAL. - Untented via flag set - Production files

- Added some silkscreen flair

- Crystal oscillator layout, isolated ground
pour, ground perimeter

- Broke out unused STM32 pins to vias

- Added pin 1 indicator to JTAG header ___________________________________ Fixed

- Add ground pour underneath uC

- Changed VBUS to VUSB

- Added 3D models to some footprints
missing them

- Changed gain of ECG chain to x10 from

- Compiled entire schematic into single sheet

THIS DESIGN AND/OR DRAWING IS THE PROPERTY OF RYAN DYNAMICS

AND SHALL NOTBE REPRODUCED WITHOUT AUTHORISATION.

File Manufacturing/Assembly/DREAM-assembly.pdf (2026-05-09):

DREAM | ASSEMBLY | DOCUMENT

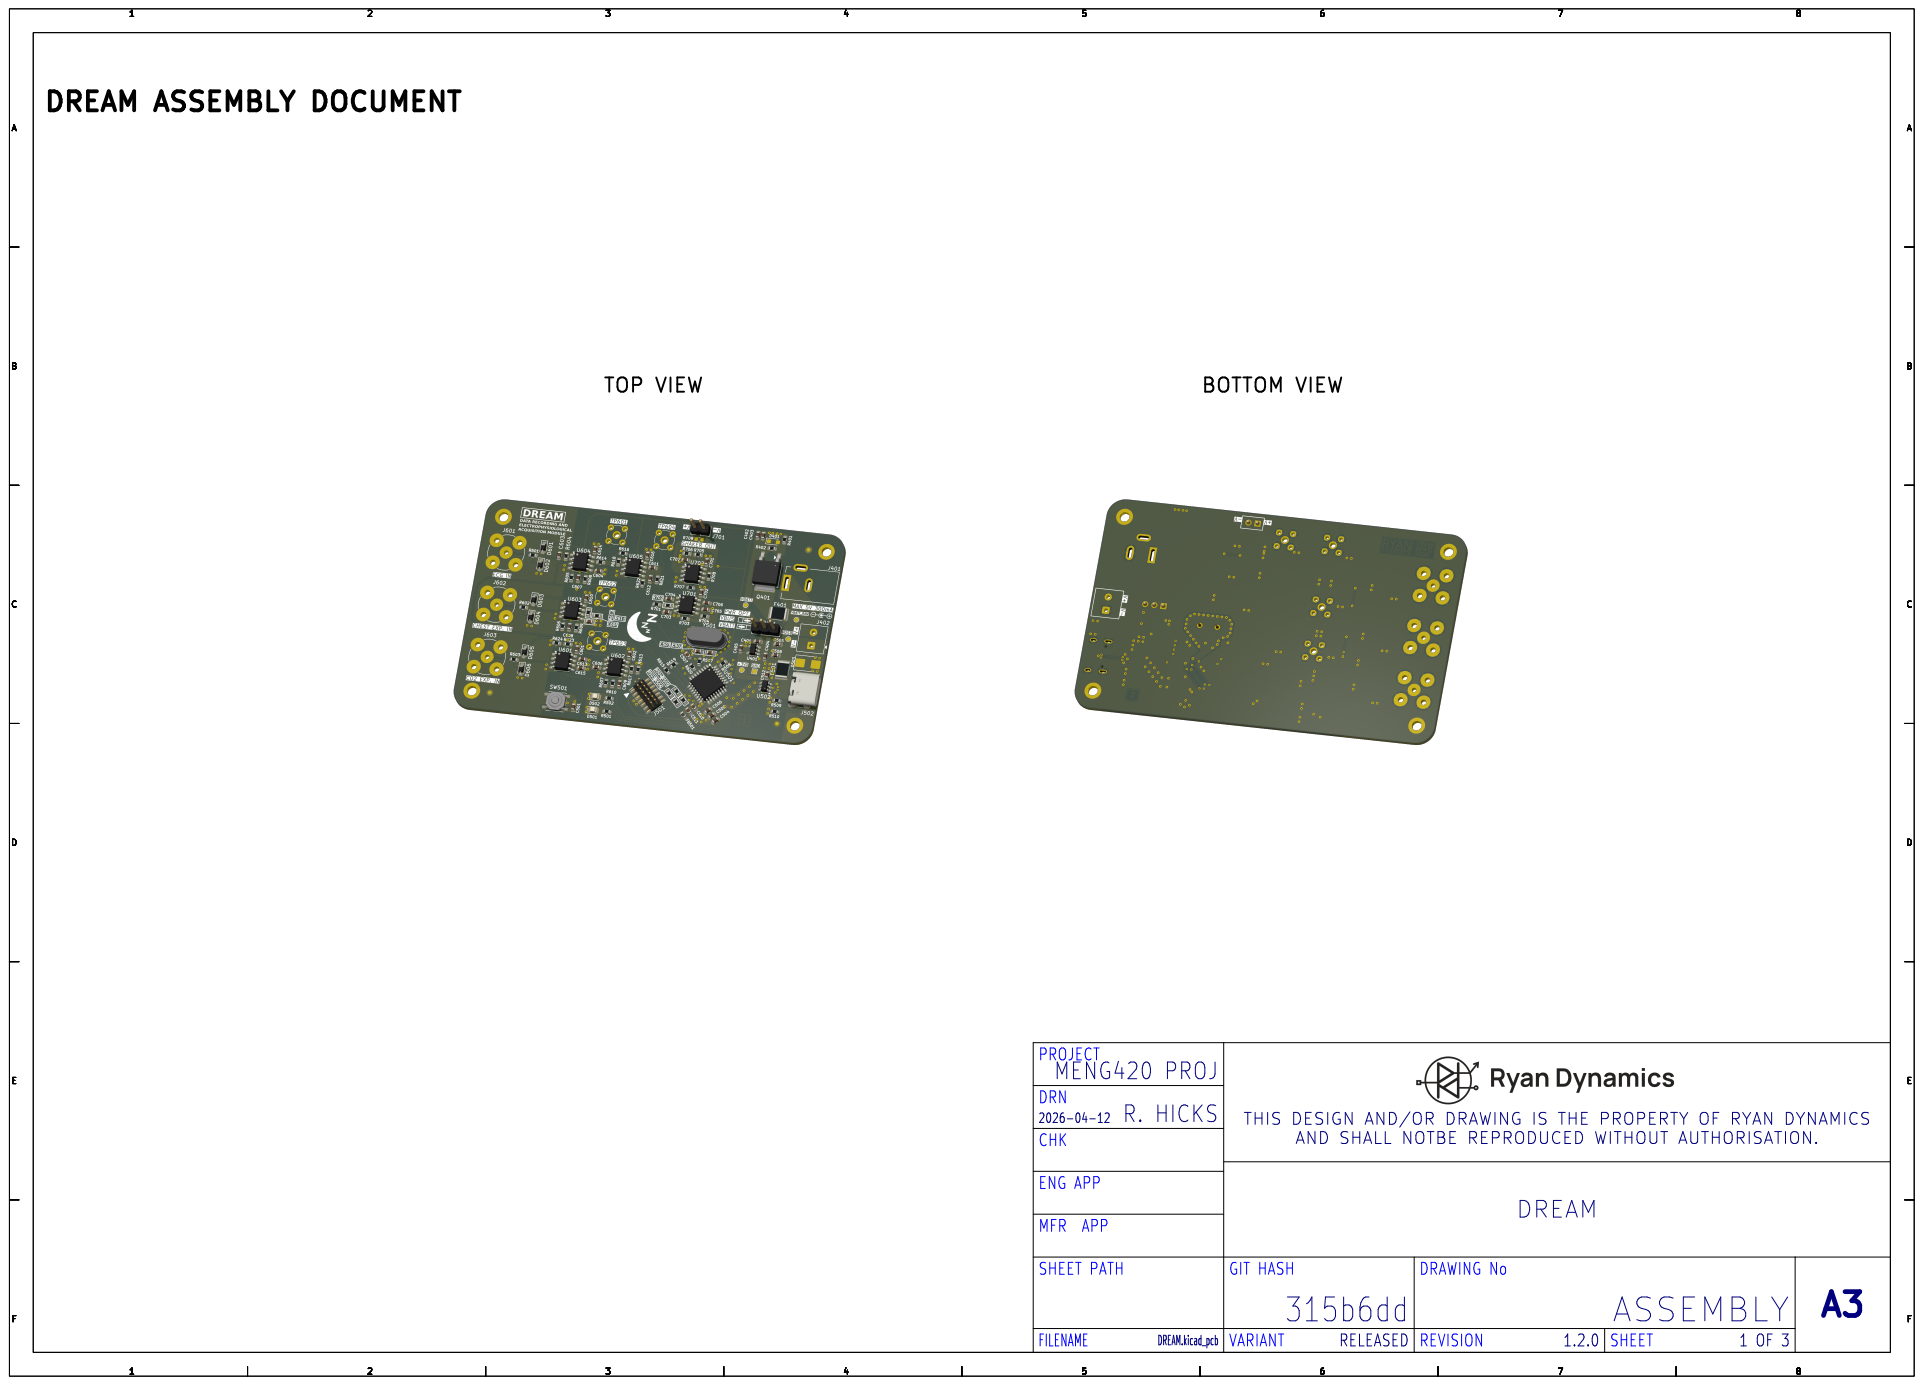
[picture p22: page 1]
DRAWING No; MENG420; PROJ; SHEET; ASSEMBLY; PROJECT; DREAM.kicad_pcb; DREAM; FILENAME; ENG APP; RELEASED; 2026-04-12 CHK; GIT; HASH; VARIANT; PATH; MFR; APP; DRN; REVISION; R. HICKS; THIS DESIGN AND/OR; DRAWING IS THE PROPERTY OF RYAN DYNAMICSAND SHALL NOTBE REPRODUCED WITHOUT AUTHORISATION.; PCB Edge; TOP VIEW; BOTTOM; VIEW

# TOP ASSEMBLY (SCALE 1:1)

# DREAM ASSEMBLY DOCUMENT

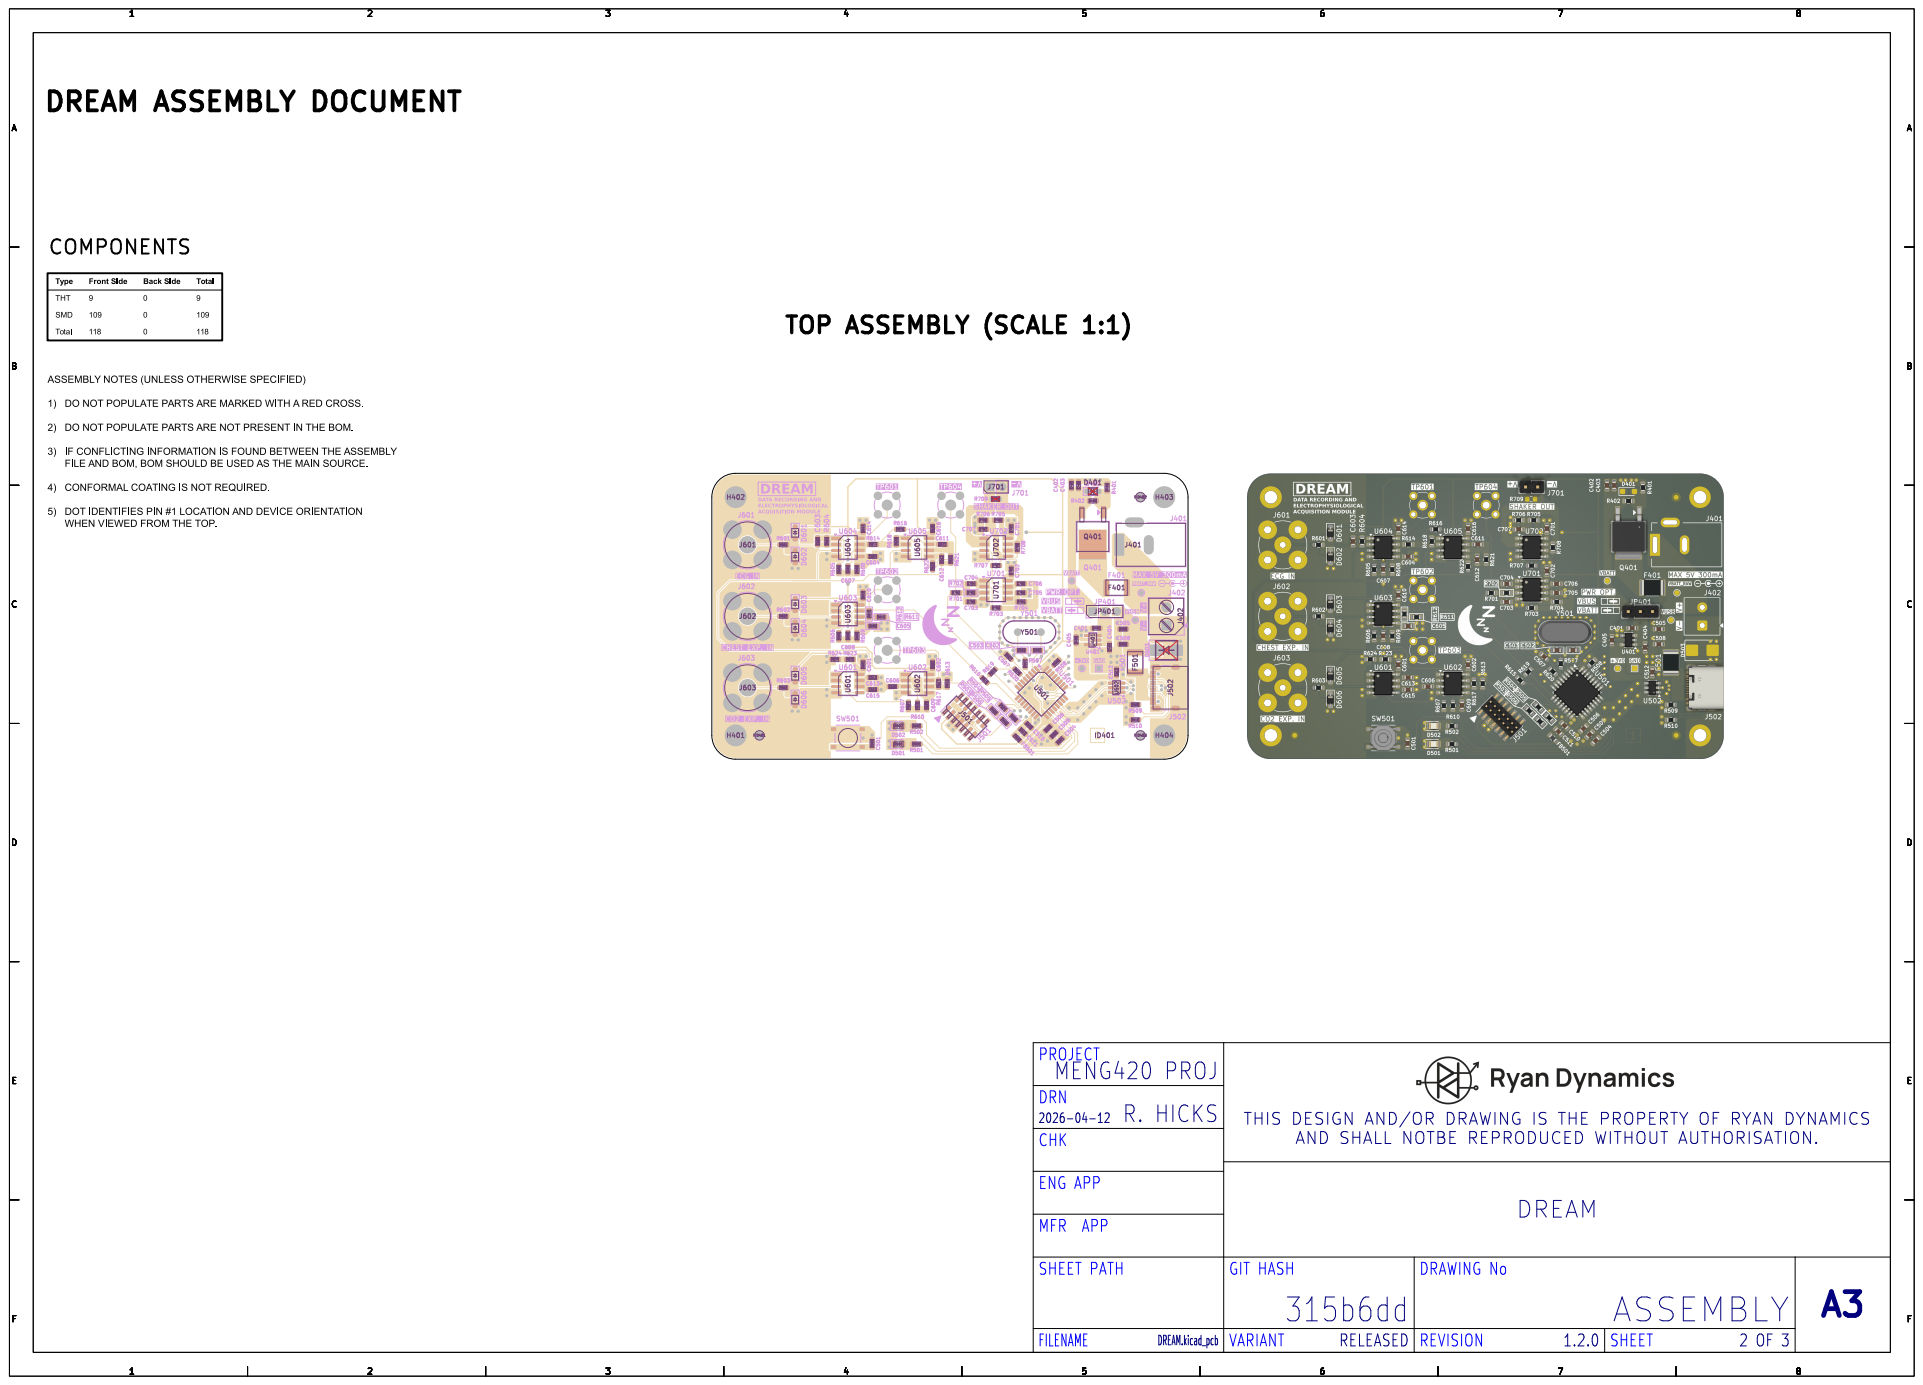
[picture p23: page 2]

PROJECT
MENG420 PROJ
DRN
THIS DESIGN AND/OR DRAWING IS THE PROPERTY OF RYAN DYNAMICSAND SHALL NOTBE REPRODUCED WITHOUT AUTHORISATION.
CHK

BOTTOM ASSEMBLY | (SCALE | 1:1)
DREAM | ASSEMBLY | DOCUMENT

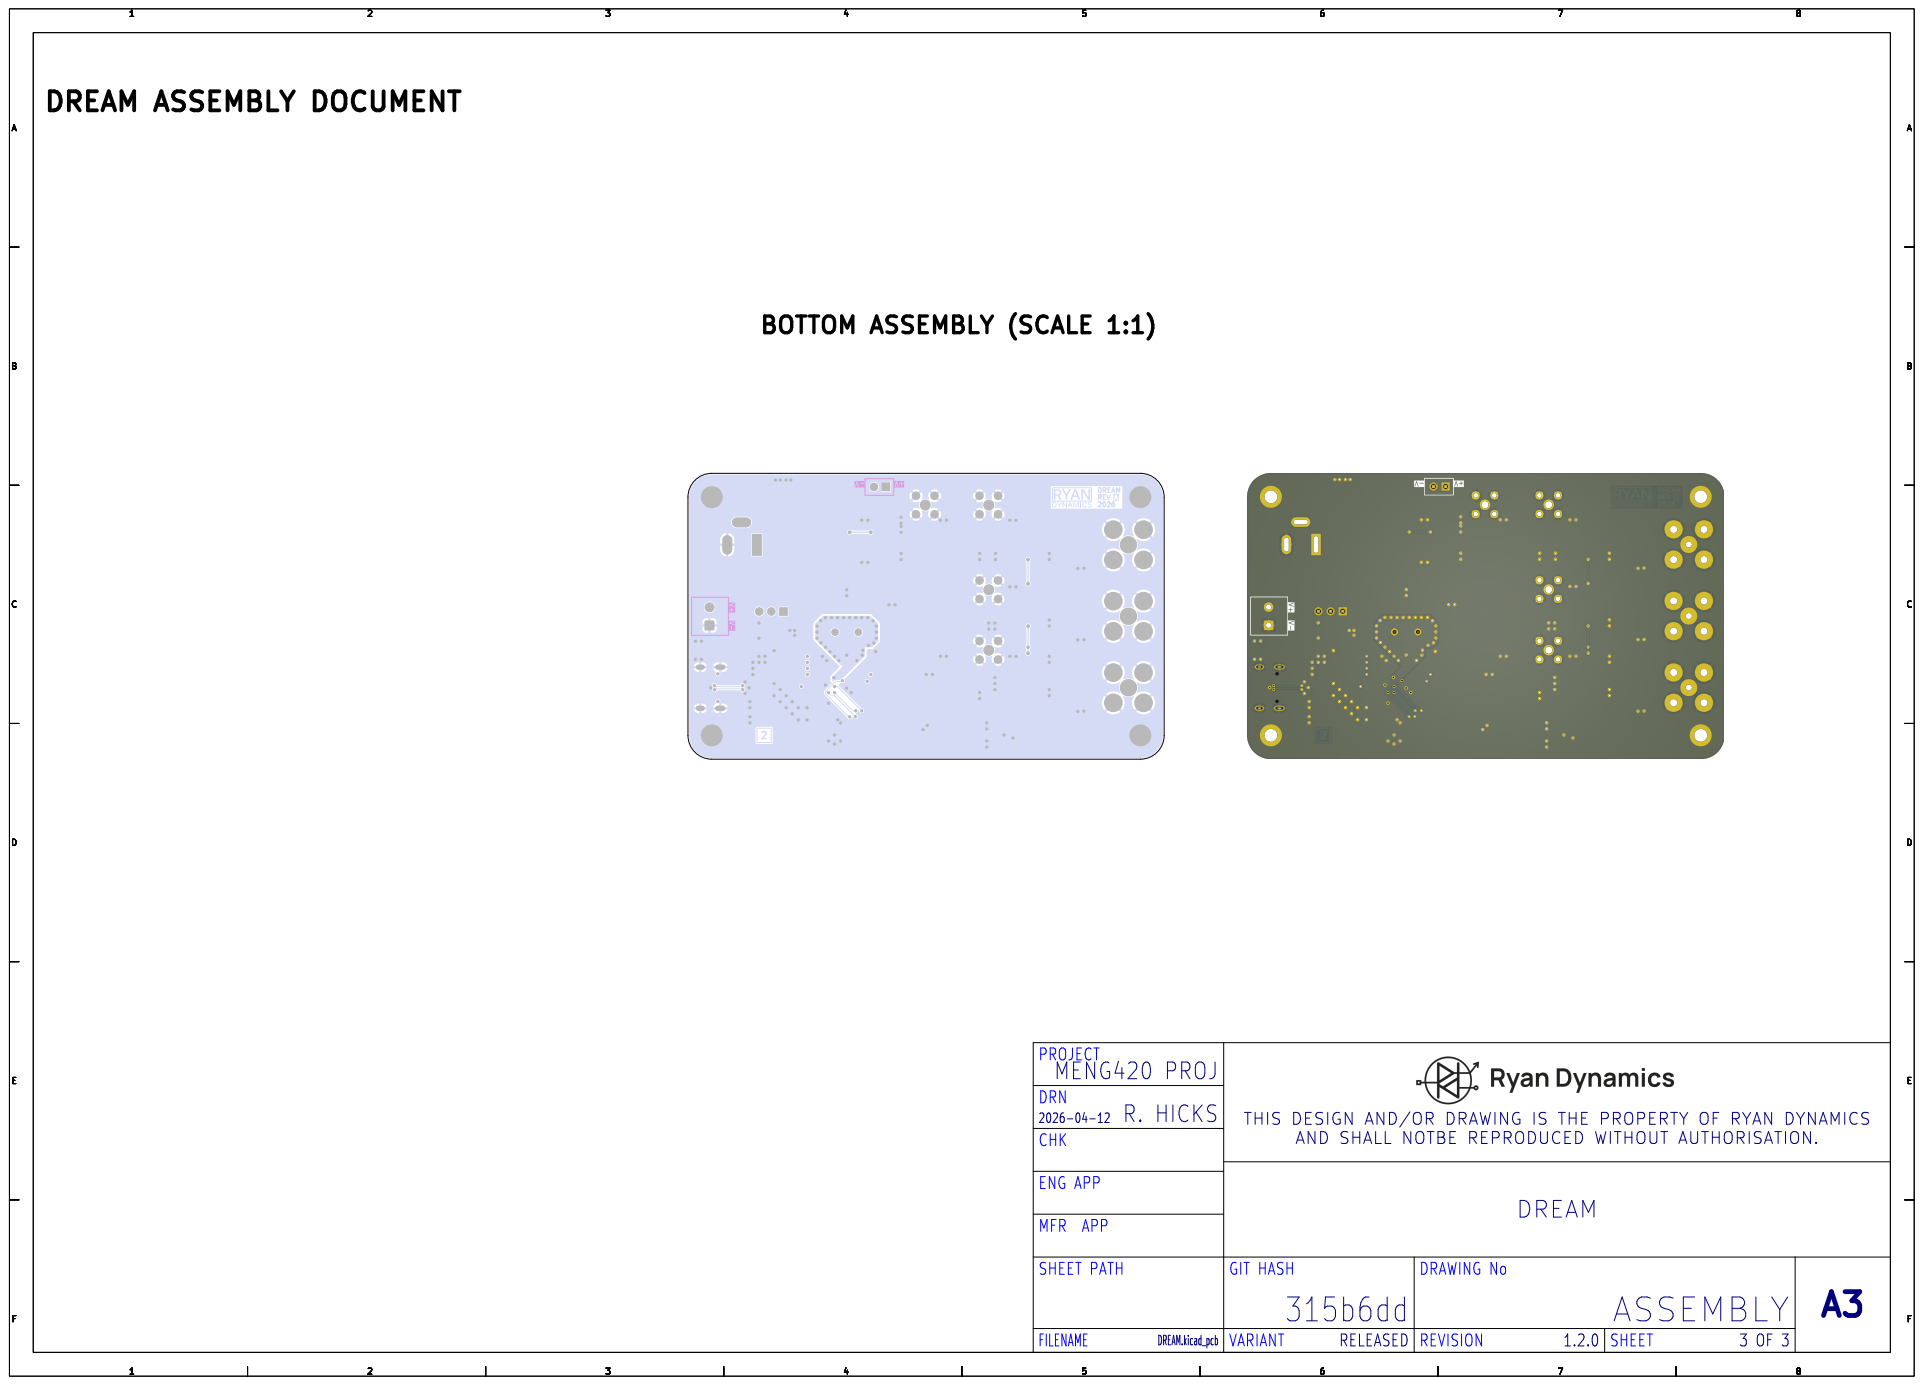
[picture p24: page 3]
DRAWING No; MENG420; PROJ; PROJECT; DREAM; ENG APP; 2026-04-12 CHK; GIT; HASH; SHEET; PATH; MFR; APP; DRN; R. HICKS; THIS DESIGN AND/OR; DRAWING IS THE PROPERTY OF RYAN DYNAMICSAND SHALL NOTBE REPRODUCED WITHOUT AUTHORISATION.; REV

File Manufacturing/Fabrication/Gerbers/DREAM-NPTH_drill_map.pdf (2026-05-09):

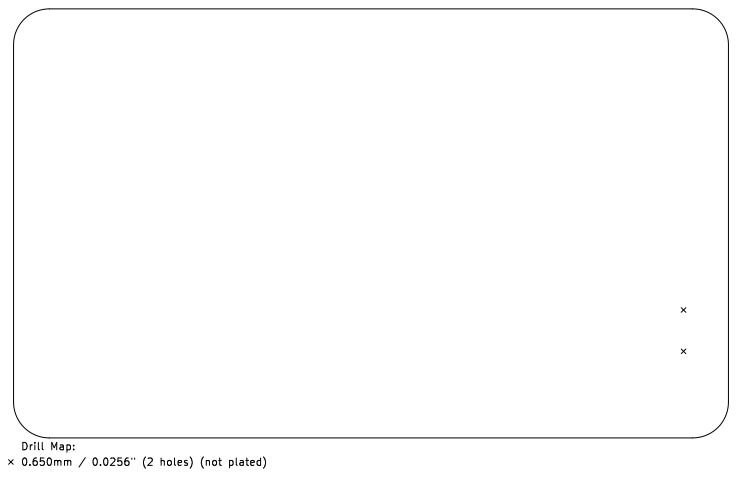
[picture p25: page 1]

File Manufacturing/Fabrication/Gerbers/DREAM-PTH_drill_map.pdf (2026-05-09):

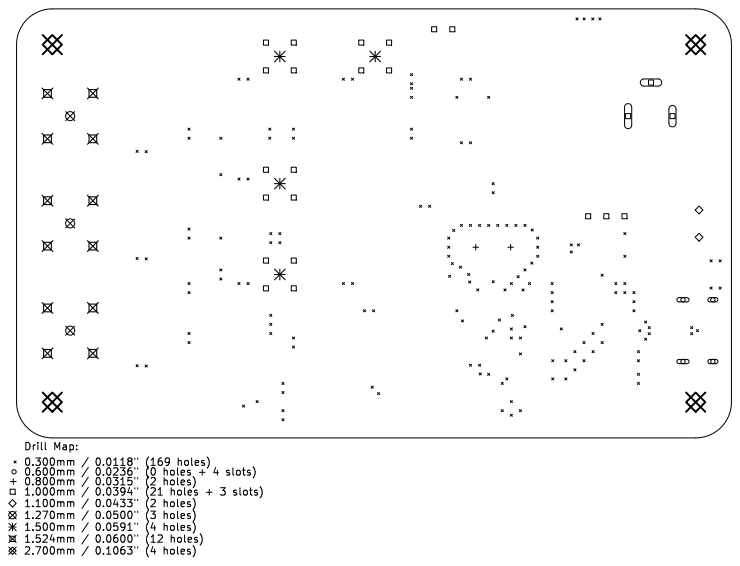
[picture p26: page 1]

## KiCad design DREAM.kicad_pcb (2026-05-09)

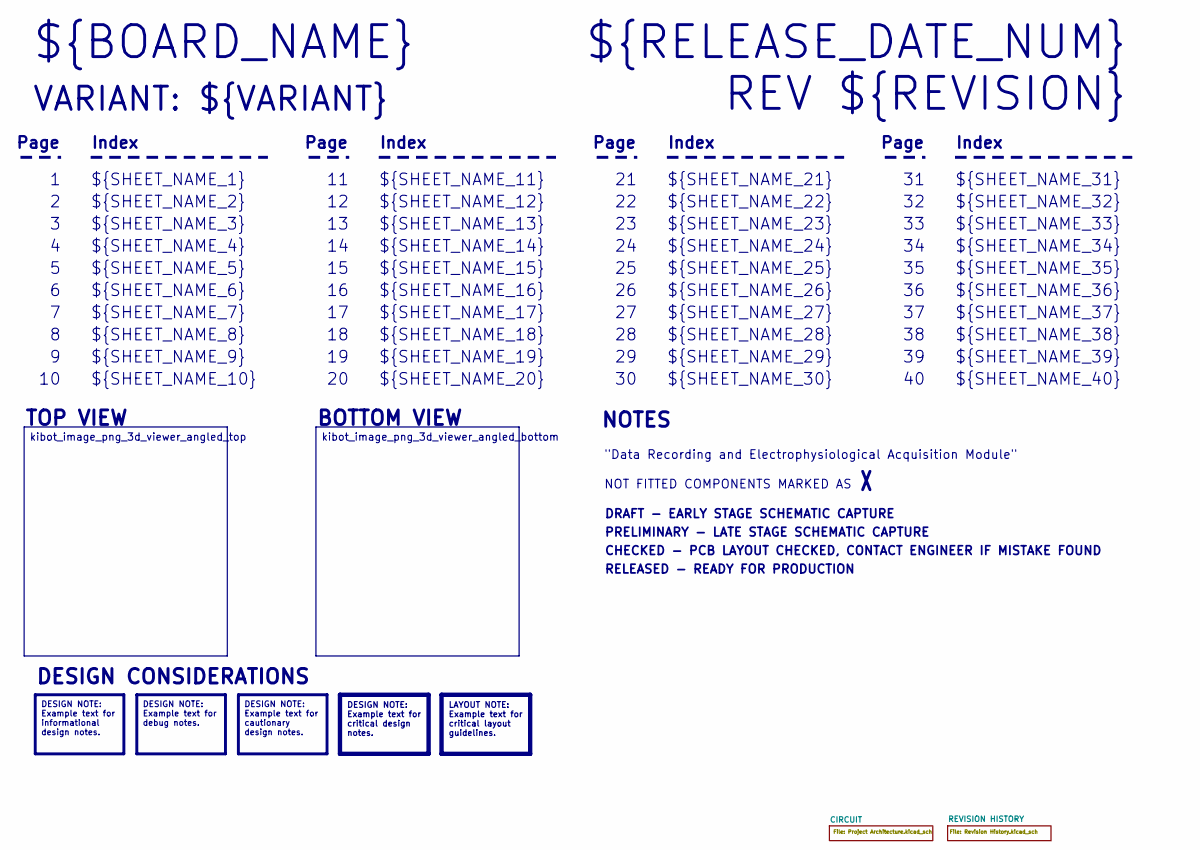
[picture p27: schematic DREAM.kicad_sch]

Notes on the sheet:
VARIANT: ${VARIANT}
RELEASED - READY FOR PRODUCTION
${SHEET_NAME_24}
Index
Page
PRELIMINARY - LATE STAGE SCHEMATIC CAPTURE
${SHEET_NAME_22}
DRAFT - EARLY STAGE SCHEMATIC CAPTURE
${SHEET_NAME_12}
${SHEET_NAME_8}
${SHEET_NAME_2}
${SHEET_NAME_5}
${SHEET_NAME_20}
${SHEET_NAME_23}
${RELEASE_DATE_NUM}
${SHEET_NAME_35}
NOT FITTED COMPONENTS MARKED AS
${SHEET_NAME_11}
${SHEET_NAME_6}
${SHEET_NAME_37}
${SHEET_NAME_26}
${SHEET_NAME_36}
REV ${REVISION}
${SHEET_NAME_15}
CHECKED - PCB LAYOUT CHECKED, CONTACT ENGINEER IF MISTAKE FOUND
BOTTOM VIEW
${SHEET_NAME_14}
${SHEET_NAME_21}
${SHEET_NAME_17}
${SHEET_NAME_18}
${SHEET_NAME_7}
${SHEET_NAME_31}
${BOARD_NAME}
NOTES
${SHEET_NAME_40}
${SHEET_NAME_39}
${SHEET_NAME_32}
${SHEET_NAME_1}
${SHEET_NAME_9}
${SHEET_NAME_38}

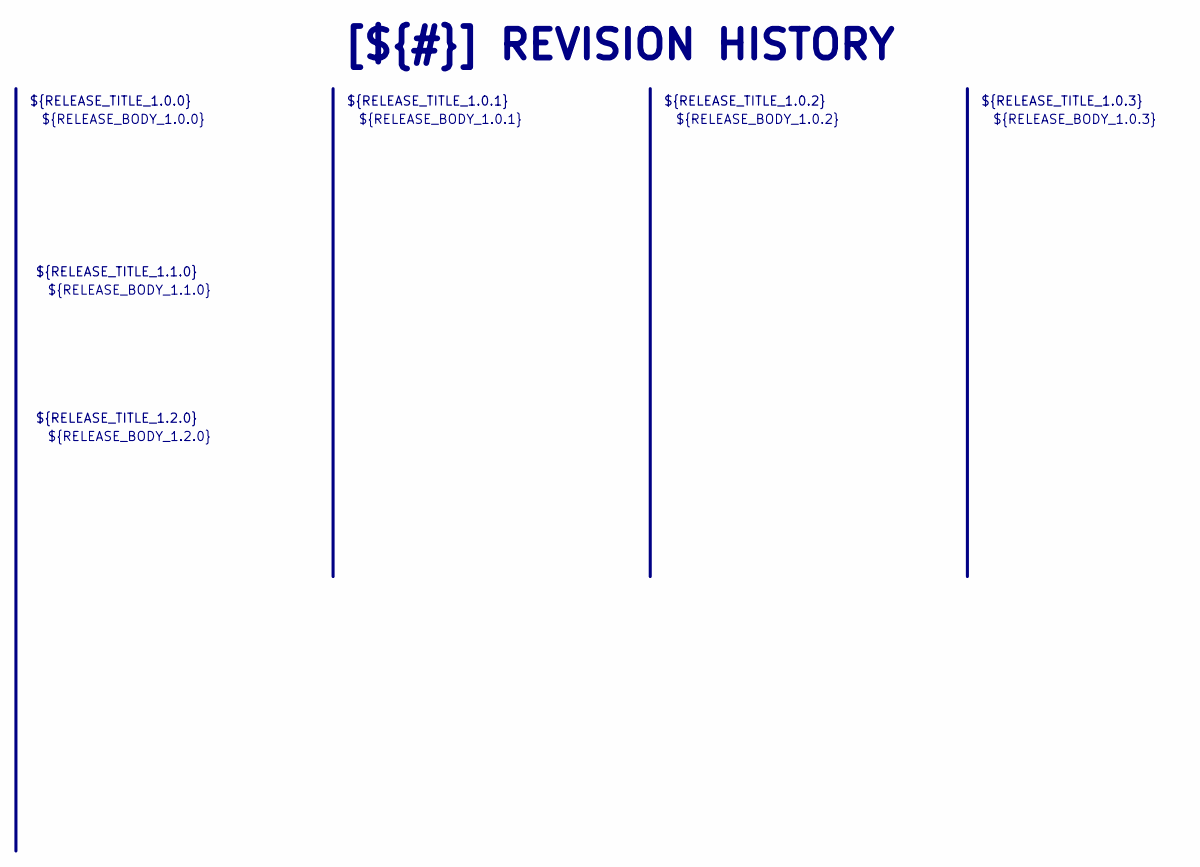
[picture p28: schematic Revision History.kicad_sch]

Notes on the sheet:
${RELEASE_BODY_1.0.3}
${RELEASE_TITLE_1.1.0}
[${#}] ${TITLE}
${RELEASE_BODY_1.0.0}
${RELEASE_TITLE_1.0.2}
${RELEASE_TITLE_1.2.0}
${RELEASE_BODY_1.0.2}
${RELEASE_BODY_1.0.1}
${RELEASE_BODY_1.1.0}
${RELEASE_BODY_1.2.0}
${RELEASE_TITLE_1.0.0}
${RELEASE_TITLE_1.0.1}
${RELEASE_TITLE_1.0.3}

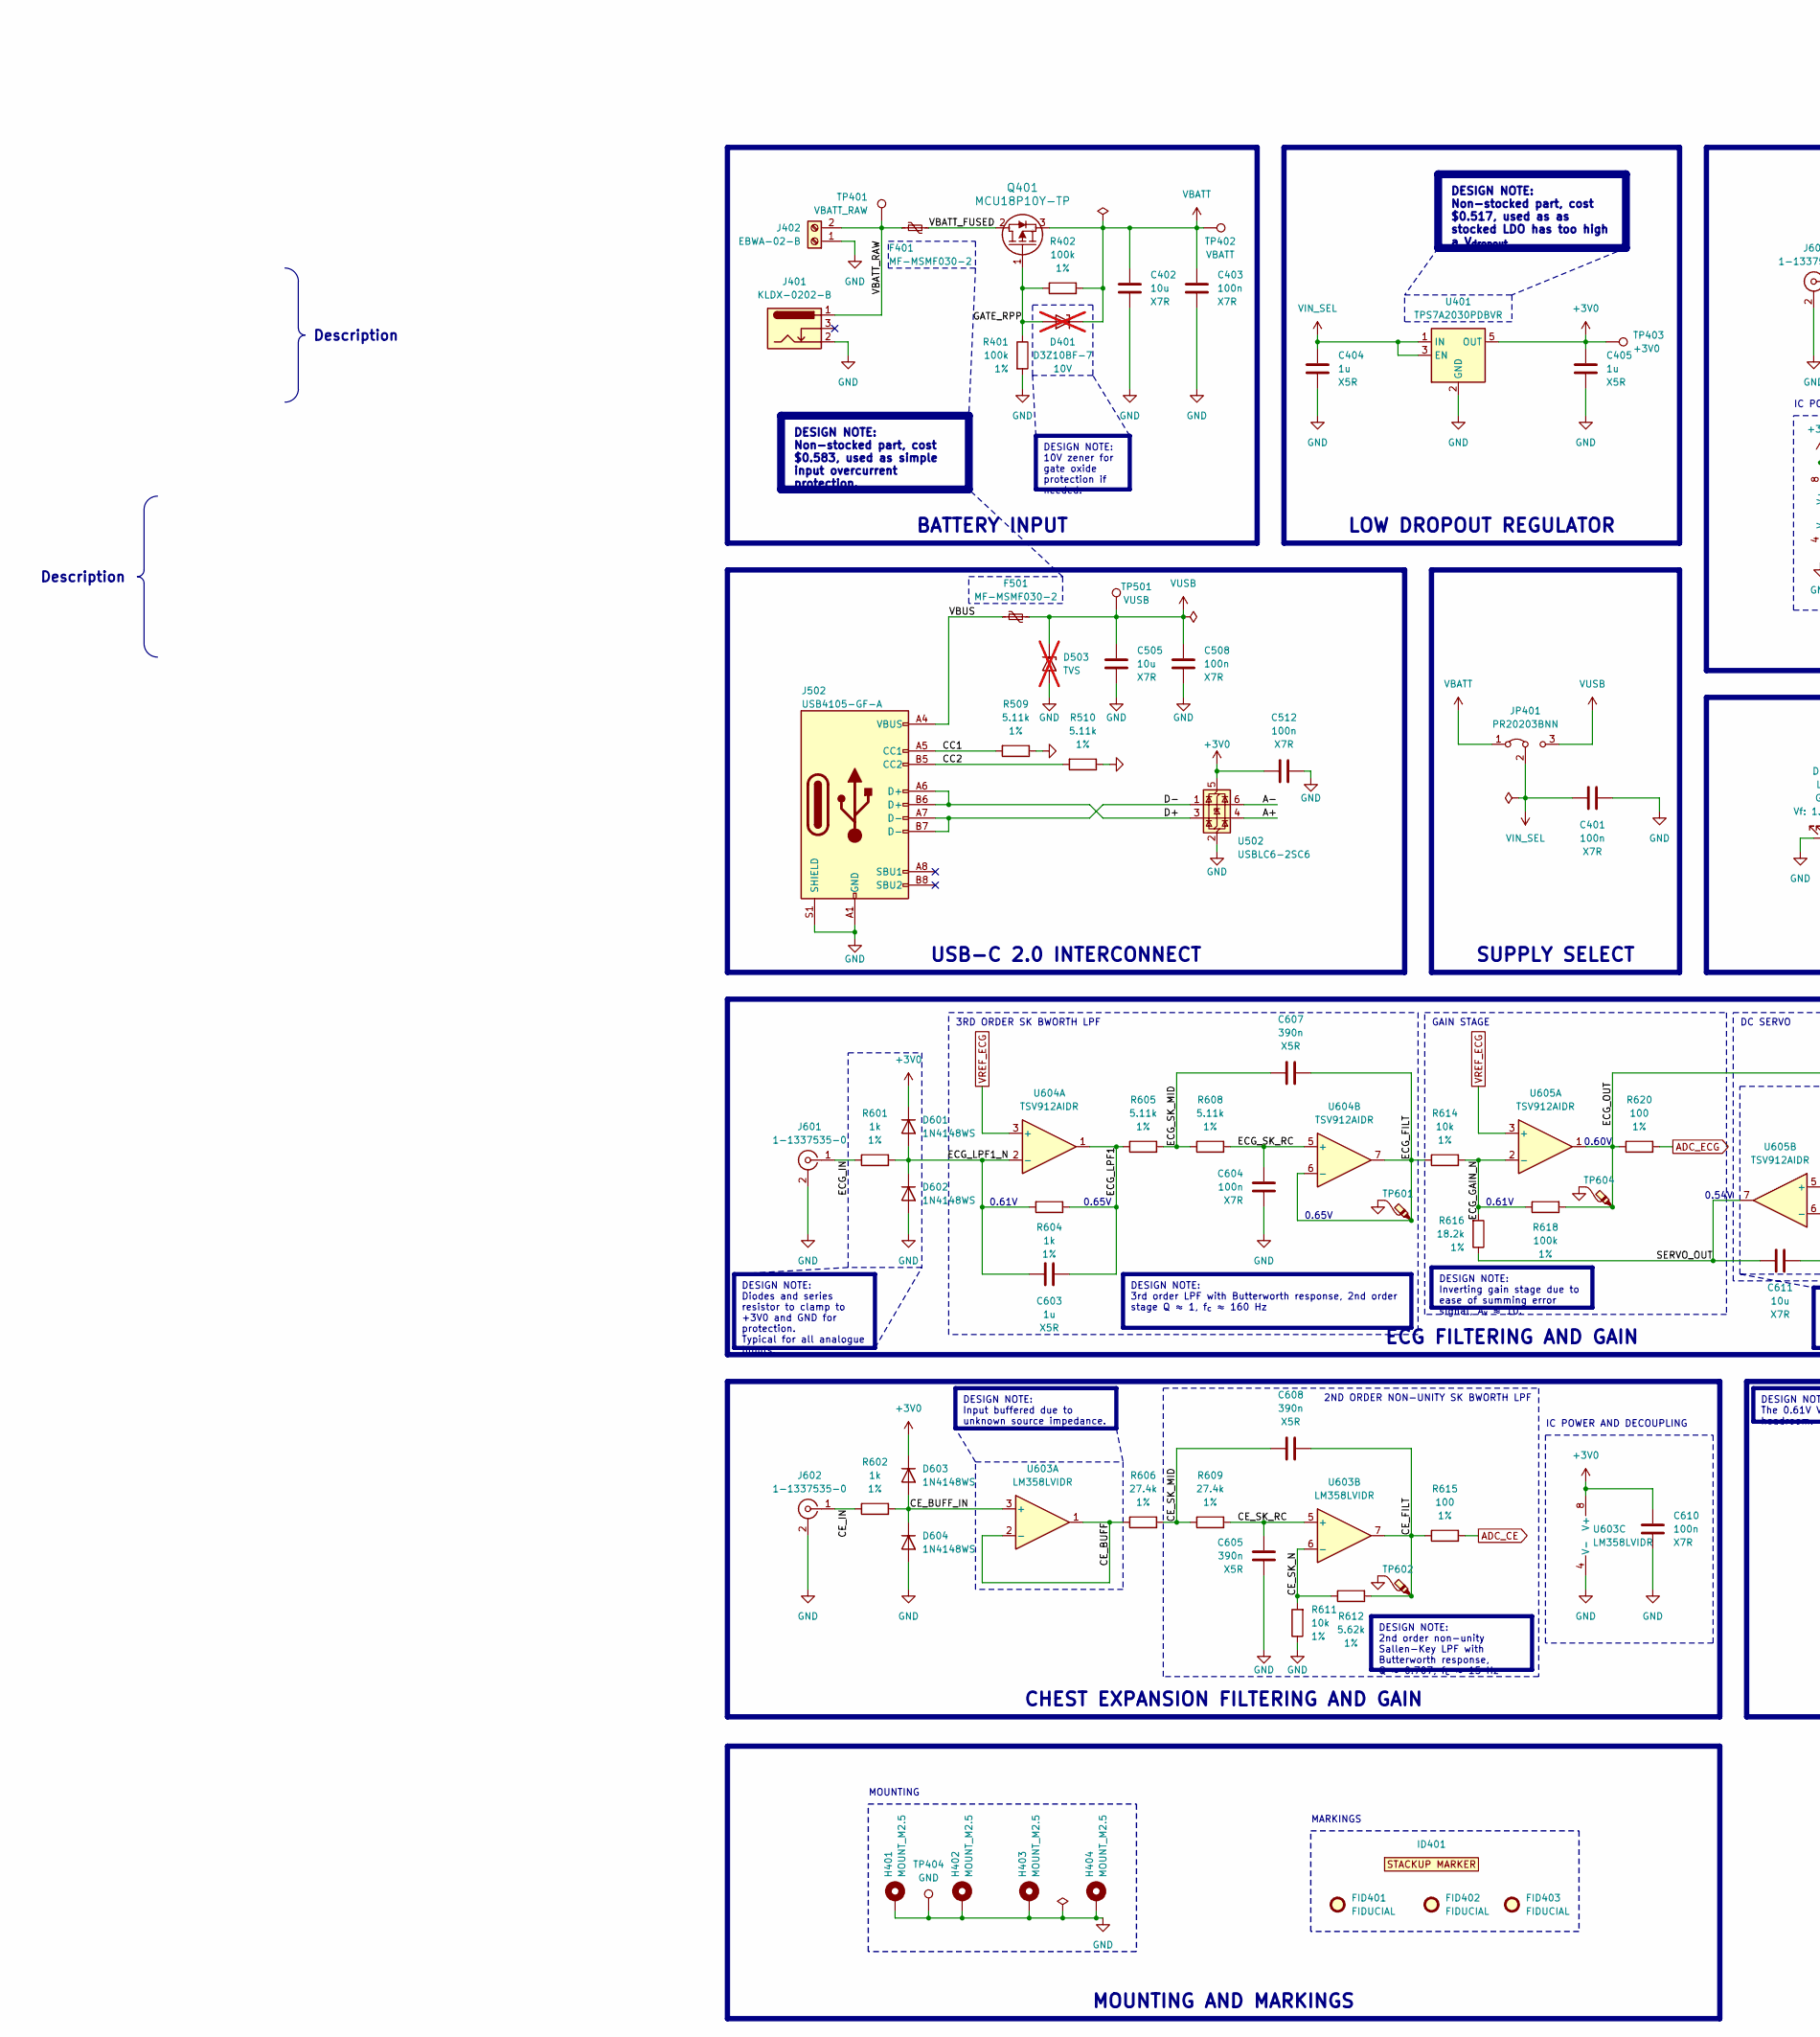
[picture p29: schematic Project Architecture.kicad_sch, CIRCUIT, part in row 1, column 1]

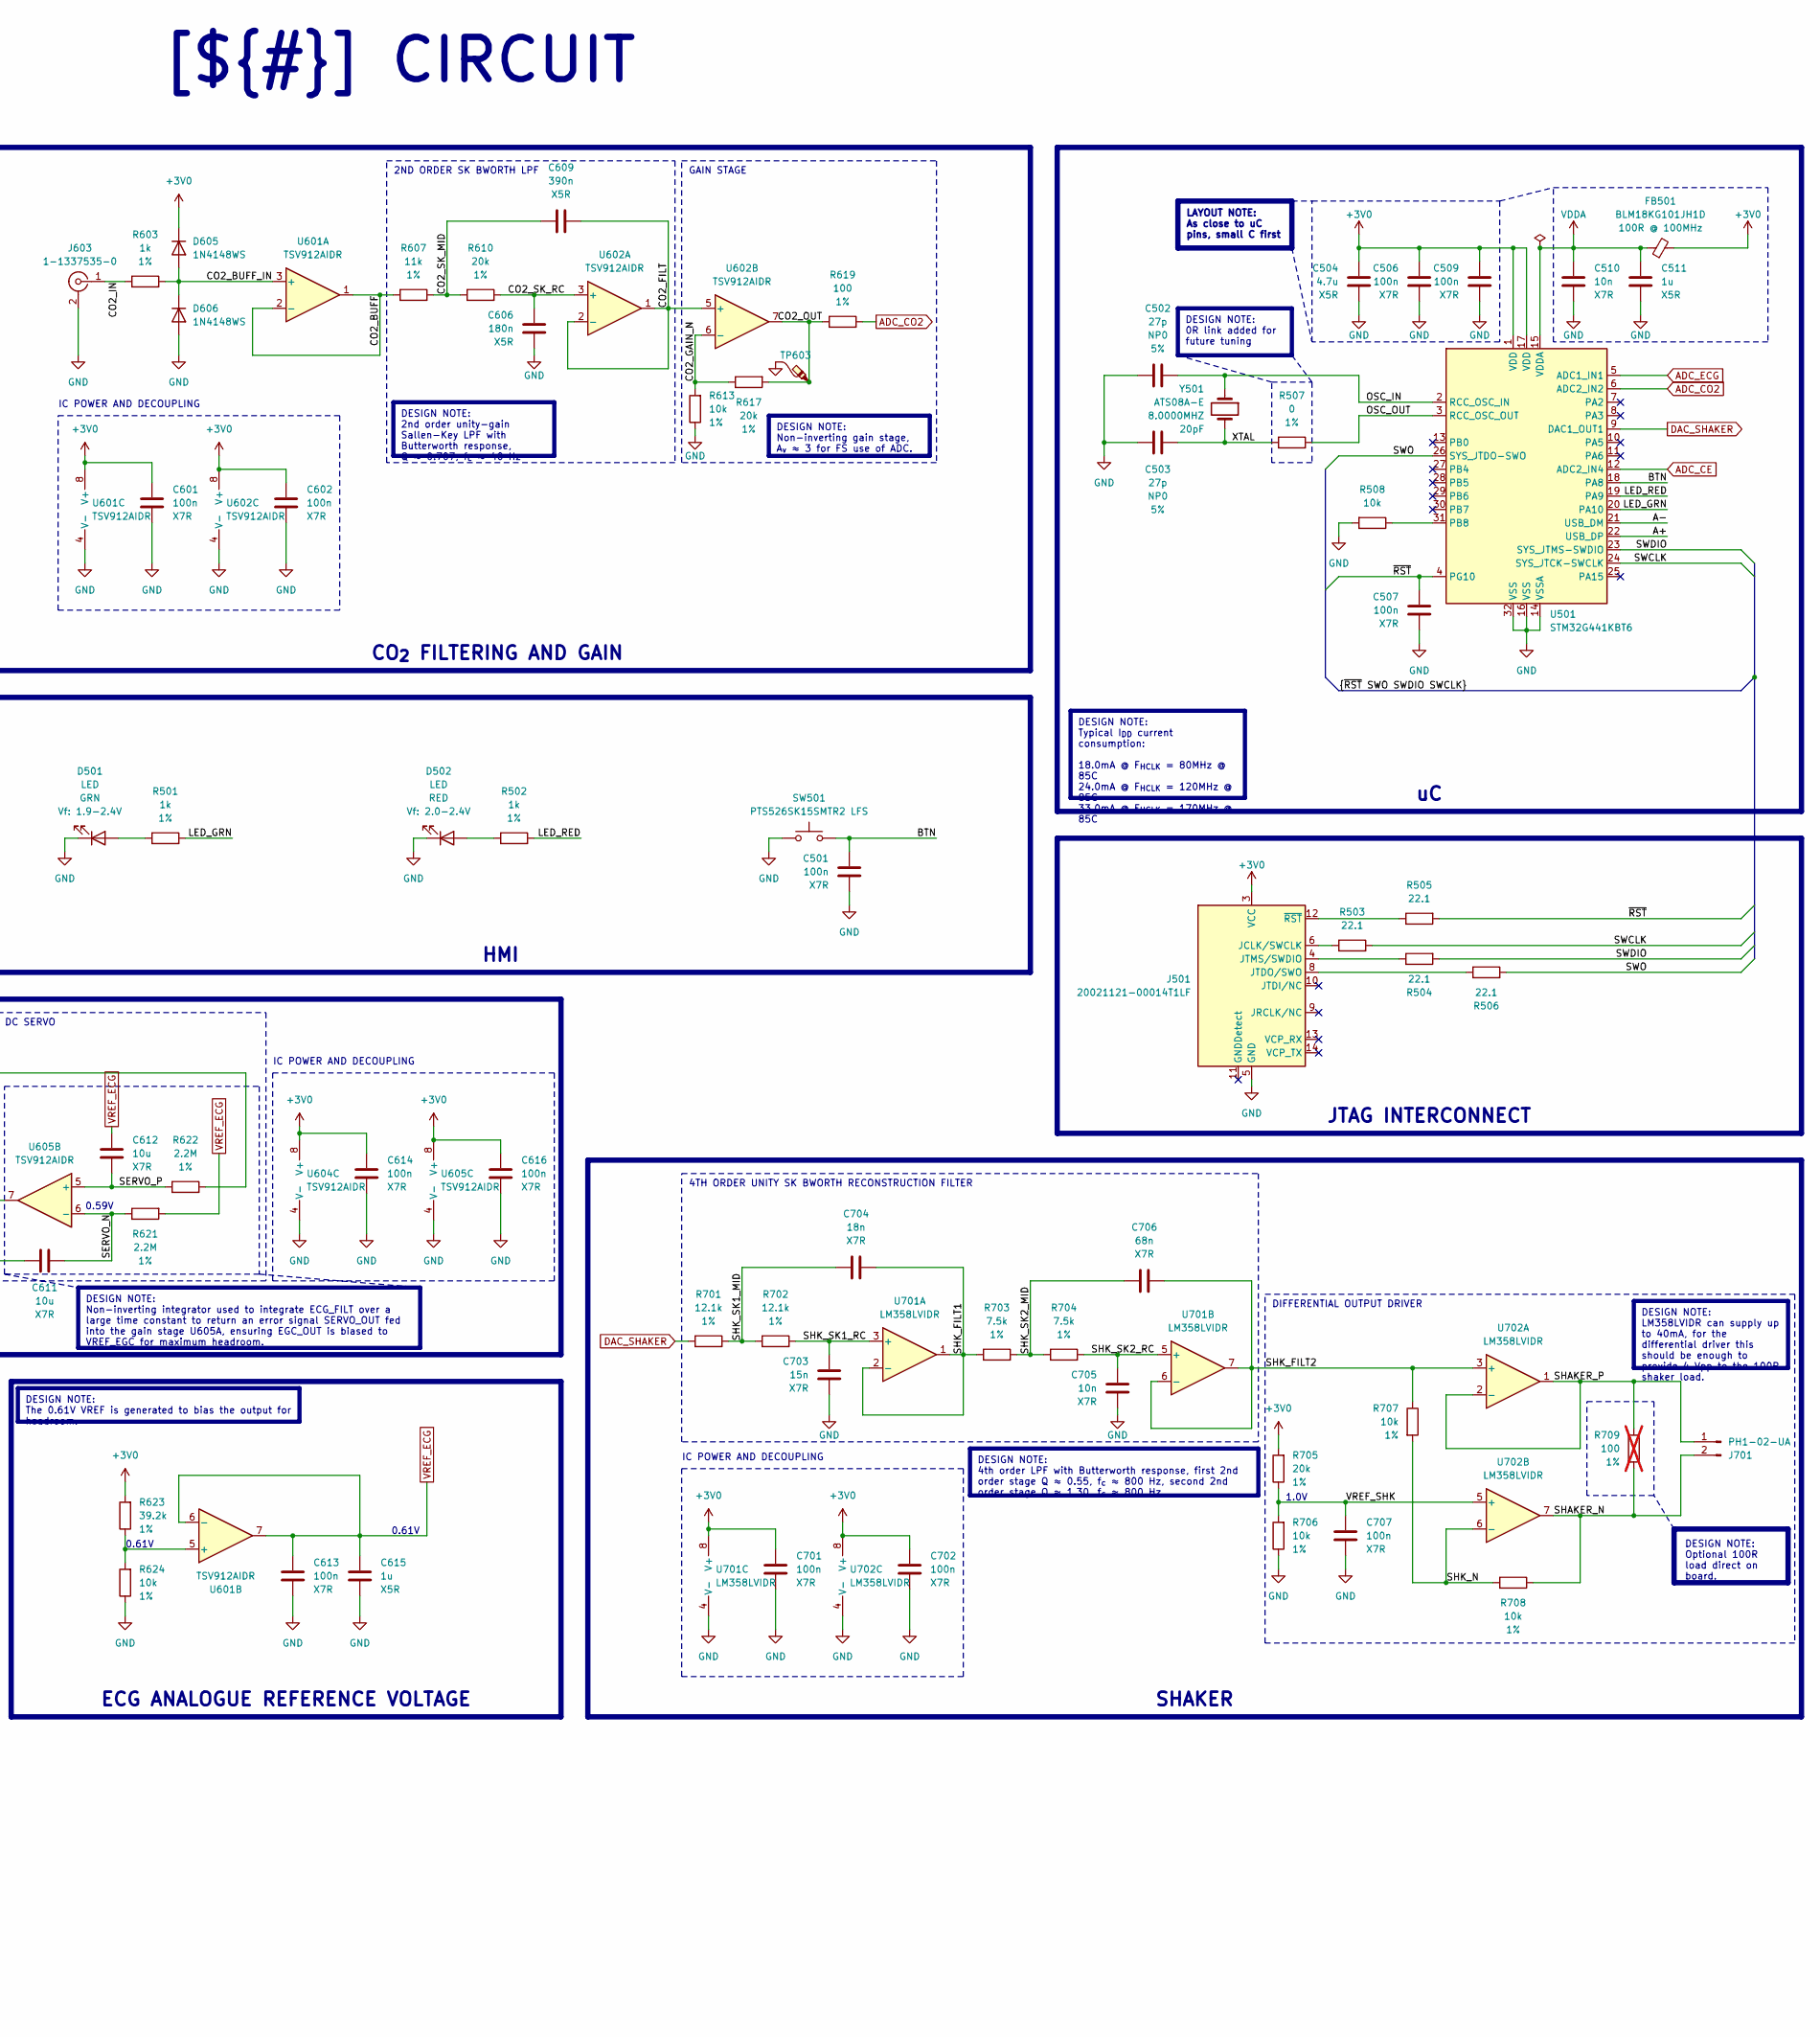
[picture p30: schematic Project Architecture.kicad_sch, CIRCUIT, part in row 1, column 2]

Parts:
C401, C403, C501, C506, C507, C508, C509, C512, C601, C602, C604, C610, C613, C614, C616, C701, C702, C707: 100n; C_0603_1608Metric; Voltage_Rating 16V; Tolerance 10%; MPN C1608X7R1C104KT
C402, C505, C611, C612: 10u; C_0603_1608Metric; Voltage_Rating 6.3V; Tolerance 10%; MPN C1608X7R0J106KT
C404, C405, C511, C603, C615: 1u; C_0603_1608Metric; Voltage_Rating 6.3V; Tolerance 10%; MPN C1608X5R0J105KT
C502, C503: 27p; C_0603_1608Metric; Voltage_Rating 50V; Tolerance 5%; MPN C1608COG1H270JT
C504: 4.7u; C_0603_1608Metric; Voltage_Rating 6.3V; Tolerance 10%; MPN C1608X5R0J475MT
C510, C705: 10n; C_0603_1608Metric; Voltage_Rating 50V; Tolerance 10%; MPN C1608X7R1H103KT
C605, C607, C608, C609: 390n; C_0603_1608Metric; Voltage_Rating 10V; Tolerance 10%; MPN C1608X5R1A394KT
C606: 180n; C_0603_1608Metric; Voltage_Rating 10V; Tolerance 10%; MPN C1608X5R1A184KT
C703: 15n; C_0603_1608Metric; Voltage_Rating 50V; Tolerance 10%; MPN C1608X7R1H153KT
C704: 18n; C_0603_1608Metric; Voltage_Rating 16V; Tolerance 10%; MPN C1608X7R1C183KT
C706: 68n; C_0603_1608Metric; Voltage_Rating 16V; Tolerance 10%; MPN C1608X7R1C683KT
D401: D3Z10BF-7; D_SOD-323_HandSoldering; MPN D3Z10BF-7; not fitted
D501: LED; LED_0805_2012Metric; MPN LTST-C170KGKT
D502: LED; LED_0805_2012Metric; MPN LTST-C170KRKT
D503: TVS; D_SMB; not fitted
D601, D602, D603, D604, D605, D606: 1N4148WS; D_SOD-323_HandSoldering; MPN 1N4148WS
F401, F501: MF-MSMF030-2; R_1812_4532Metric; Voltage 30V; MPN Bourns Inc.
FB501: BLM18KG101JH1D; L_0603_1608Metric; MPN BLM18KG101JH1D
FID401, FID402, FID403: FIDUCIAL; Fiducial_1mm_Mask2mm
H401, H402, H403, H404: MOUNT_M2.5; MountingHole_2.7mm_M2.5_ISO7380_Pad
ID401: BOARD_STACKUP_MARKER; STACKUP_ID_2L
J401: KLDX-0202-B; BarrelJack_Kycon_KLDX-0202-xC_Horizontal; MPN KLDX-0202-B
J402: EBWA-02-B; TerminalBlock_Phoenix_MKDS-1-2-3.81_1x02_P3.81mm_Horizontal; MPN EBWA-02-B
J501: 20021121-00014T1LF; PinHeader_2x07_P1.27mm_Vertical_SMD; MPN 20021121-00014T1LF
J502: USB4105-GF-A; USB_C_Receptacle_GCT_USB4105-xx-A_16P_TopMnt_Horizontal; MPN USB4105-GF-A
J601, J602, J603: 1-1337535-0; BNC_TEConnectivity_1478204_Vertical; MPN 1-1337535-0
J701: PH1-02-UA; PinHeader_1x02_P2.54mm_Vertical
JP401: PR20203BNN; PinHeader_1x03_P2.54mm_Vertical; MPN PR20203BNN
Q401: MCU18P10Y-TP; DPAK_MCC; MPN MCU18P10Y-TP
R401, R402, R618: 100k; R_0603_1608Metric; Tolerance 1%
R501, R502, R601, R602, R603, R604: 1k; R_0603_1608Metric; Tolerance 1%
R503, R504, R505, R506: 22.1; R_0603_1608Metric; Tolerance 1%
R507: 0; R_0603_1608Metric; Tolerance 1%
R508, R611, R613, R614, R624, R706, R707, R708: 10k; R_0603_1608Metric; Tolerance 1%
R509, R510, R605, R608: 5.11k; R_0603_1608Metric; Tolerance 1%
R606, R609: 27.4k; R_0603_1608Metric; Tolerance 1%
R607: 11k; R_0603_1608Metric; Tolerance 1%
R610, R617, R705: 20k; R_0603_1608Metric; Tolerance 1%
R612: 5.62k; R_0603_1608Metric; Tolerance 1%
R615, R619, R620: 100; R_0603_1608Metric; Tolerance 1%
R616: 18.2k; R_0603_1608Metric; Tolerance 1%
R621, R622: 2.2M; R_0603_1608Metric; Tolerance 1%
R623: 39.2k; R_0603_1608Metric; Tolerance 1%
R701, R702: 12.1k; R_0603_1608Metric; Tolerance 1%
R703, R704: 7.5k; R_0603_1608Metric; Tolerance 1%
R709: 100; R_0603_1608Metric; Tolerance 1%; not fitted
SW501: PTS526SK15SMTR2 LFS; SW_SPST_PTS526xxxSMTR; MPN PTS526SK15SMTR2 LFS
TP401: VBATT_RAW; TestPoint_Pad_D1.0mm
TP402: VBATT; TestPoint_Pad_D1.0mm
TP403: +3V0; TestPoint_Pad_D1.0mm
TP404: GND; TestPoint_Pad_1.0x1.0mm
TP501: VUSB; TestPoint_Pad_D1.0mm
TP601, TP602, TP603, TP604: TestPoint_PMK_Probe; TestPoint_THTPad_PMK
U401: TPS7A2030PDBVR; SOT-23-5; MPN TPS7A2030PDBVR
U501: STM32G441KBT6; LQFP-32_7x7mm_P0.8mm; MPN STM32G441KBT6
U502: USBLC6-2SC6; SOT-23-6; MPN USBLC6-2SC6
U601, U602, U604, U605: TSV912AIDR; SOIC-8_3.9x4.9mm_P1.27mm; MPN TSV912AIDR
U603, U701, U702: LM358LVIDR; SOIC-8_3.9x4.9mm_P1.27mm; MPN LM358LVIDR
Y501: ATS08A-E; Crystal_HC49-4H_Vertical; MPN ATS08A-E

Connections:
+3V0: C405.2, C504.2, C506.2, C509.2, C512.2, C601.1, C602.1, C610.1, C614.1, C616.1, C701.1, C702.1, D601.1 (K), D603.1 (K), D605.1 (K), FB501.2, J501.3 (VCC), R623.2, R705.2, TP403.1, U401.5 (OUT), U501.1 (VDD), U501.17 (VDD), U502.5 (VBUS), U601.8 (V+), U602.8 (V+), U603.8 (V+), U604.8 (V+), U605.8 (V+), U701.8 (V+), U702.8 (V+)
/ARCHITECTURE/ANALOGUE INPUTS/ADC_CE: R615.2, U501.12 (ADC2_IN4)
/ARCHITECTURE/ANALOGUE INPUTS/ADC_CO2: R619.2, U501.6 (ADC2_IN2)
/ARCHITECTURE/ANALOGUE INPUTS/ADC_ECG: R620.2, U501.5 (ADC1_IN1)
/ARCHITECTURE/ANALOGUE INPUTS/CE_BUFF: R606.1, U603.1, U603.2 (-)
/ARCHITECTURE/ANALOGUE INPUTS/CE_BUFF_IN: D603.2 (A), D604.1 (K), R602.2, U603.3 (+)
/ARCHITECTURE/ANALOGUE INPUTS/CE_FILT: C608.1, R612.2, R615.1, TP602.1, U603.7
/ARCHITECTURE/ANALOGUE INPUTS/CE_IN: J602.1 (In), R602.1
/ARCHITECTURE/ANALOGUE INPUTS/CE_SK_MID: C608.2, R606.2, R609.1
/ARCHITECTURE/ANALOGUE INPUTS/CE_SK_N: R611.2, R612.1, U603.6 (-)
/ARCHITECTURE/ANALOGUE INPUTS/CE_SK_RC: C605.1, R609.2, U603.5 (+)
/ARCHITECTURE/ANALOGUE INPUTS/CO2_BUFF: R607.1, U601.1, U601.2 (-)
/ARCHITECTURE/ANALOGUE INPUTS/CO2_BUFF_IN: D605.2 (A), D606.1 (K), R603.2, U601.3 (+)
/ARCHITECTURE/ANALOGUE INPUTS/CO2_FILT: C609.1, U602.1, U602.2 (-), U602.5 (+)
/ARCHITECTURE/ANALOGUE INPUTS/CO2_GAIN_N: R613.2, R617.1, U602.6 (-)
/ARCHITECTURE/ANALOGUE INPUTS/CO2_IN: J603.1 (In), R603.1
/ARCHITECTURE/ANALOGUE INPUTS/CO2_OUT: R617.2, R619.1, TP603.1, U602.7
/ARCHITECTURE/ANALOGUE INPUTS/CO2_SK_MID: C609.2, R607.2, R610.1
/ARCHITECTURE/ANALOGUE INPUTS/CO2_SK_RC: C606.1, R610.2, U602.3 (+)
/ARCHITECTURE/ANALOGUE INPUTS/ECG_FILT: C607.1, R614.1, TP601.1, U604.6 (-), U604.7
/ARCHITECTURE/ANALOGUE INPUTS/ECG_GAIN_N: R614.2, R616.2, R618.1, U605.2 (-)
/ARCHITECTURE/ANALOGUE INPUTS/ECG_IN: J601.1 (In), R601.1
/ARCHITECTURE/ANALOGUE INPUTS/ECG_LPF1: C603.1, R604.1, R605.1, U604.1
/ARCHITECTURE/ANALOGUE INPUTS/ECG_LPF1_N: C603.2, D601.2 (A), D602.1 (K), R601.2, R604.2, U604.2 (-)
/ARCHITECTURE/ANALOGUE INPUTS/ECG_OUT: R618.2, R620.1, R622.2, TP604.1, U605.1
/ARCHITECTURE/ANALOGUE INPUTS/ECG_SK_MID: C607.2, R605.2, R608.1
/ARCHITECTURE/ANALOGUE INPUTS/ECG_SK_RC: C604.1, R608.2, U604.5 (+)
/ARCHITECTURE/ANALOGUE INPUTS/SERVO_N: C611.1, R621.1, U605.6 (-)
/ARCHITECTURE/ANALOGUE INPUTS/SERVO_OUT: C611.2, R616.1, U605.7
/ARCHITECTURE/ANALOGUE INPUTS/SERVO_P: C612.2, R622.1, U605.5 (+)
/ARCHITECTURE/ANALOGUE OUTPUTS/DAC_SHAKER: R701.1, U501.9 (DAC1_OUT1)
/ARCHITECTURE/ANALOGUE OUTPUTS/SHAKER_N: J701.2, R708.1, R709.2, U702.7
/ARCHITECTURE/ANALOGUE OUTPUTS/SHAKER_P: J701.1, R709.1, U702.1, U702.2 (-)
/ARCHITECTURE/ANALOGUE OUTPUTS/SHK_FILT1: C704.1, R703.1, U701.1, U701.2 (-)
/ARCHITECTURE/ANALOGUE OUTPUTS/SHK_FILT2: C706.1, R707.1, U701.6 (-), U701.7, U702.3 (+)
/ARCHITECTURE/ANALOGUE OUTPUTS/SHK_N: R707.2, R708.2, U702.6 (-)
/ARCHITECTURE/ANALOGUE OUTPUTS/SHK_SK1_MID: C704.2, R701.2, R702.1
/ARCHITECTURE/ANALOGUE OUTPUTS/SHK_SK1_RC: C703.1, R702.2, U701.3 (+)
/ARCHITECTURE/ANALOGUE OUTPUTS/SHK_SK2_MID: C706.2, R703.2, R704.1
/ARCHITECTURE/ANALOGUE OUTPUTS/SHK_SK2_RC: C705.1, R704.2, U701.5 (+)
/ARCHITECTURE/ANALOGUE OUTPUTS/VREF_SHK: C707.1, R705.1, R706.2, U702.5 (+)
/ARCHITECTURE/DIGITAL AND HMI/A+: U501.22 (USB_DP), U502.4 (I/O2)
/ARCHITECTURE/DIGITAL AND HMI/A-: U501.21 (USB_DM), U502.6 (I/O1)
/ARCHITECTURE/DIGITAL AND HMI/BTN: C501.2, SW501.2, U501.18 (PA8)
/ARCHITECTURE/DIGITAL AND HMI/CC1: J502.A5 (CC1), R509.2
/ARCHITECTURE/DIGITAL AND HMI/CC2: J502.B5 (CC2), R510.2
/ARCHITECTURE/DIGITAL AND HMI/D+: J502.A6 (D+), J502.B6 (D+), U502.3 (I/O2)
/ARCHITECTURE/DIGITAL AND HMI/D-: J502.A7 (D-), J502.B7 (D-), U502.1 (I/O1)
/ARCHITECTURE/DIGITAL AND HMI/LED_GRN: R501.2, U501.20 (PA10)
/ARCHITECTURE/DIGITAL AND HMI/LED_RED: R502.2, U501.19 (PA9)
/ARCHITECTURE/DIGITAL AND HMI/OSC_IN: C502.2, U501.2 (RCC_OSC_IN), Y501.1
/ARCHITECTURE/DIGITAL AND HMI/OSC_OUT: R507.2, U501.3 (RCC_OSC_OUT)
/ARCHITECTURE/DIGITAL AND HMI/SWCLK: R503.2, U501.24 (SYS_JTCK-SWCLK)
/ARCHITECTURE/DIGITAL AND HMI/SWDIO: R504.2, U501.23 (SYS_JTMS-SWDIO)
/ARCHITECTURE/DIGITAL AND HMI/SWO: R506.2, U501.26 (SYS_JTDO-SWO)
/ARCHITECTURE/DIGITAL AND HMI/VBUS: F501.1, J502.A4 (VBUS), J502.A9 (VBUS), J502.B4 (VBUS), J502.B9 (VBUS)
/ARCHITECTURE/DIGITAL AND HMI/VDDA: C510.2, C511.2, FB501.1, U501.15 (VDDA)
/ARCHITECTURE/DIGITAL AND HMI/XTAL: C503.1, R507.1, Y501.2
/ARCHITECTURE/DIGITAL AND HMI/~RST: C507.2, R505.2, U501.4 (PG10)
/ARCHITECTURE/POWER/GATE_RPP: D401.2 (A), Q401.1, R401.1, R402.1
/ARCHITECTURE/POWER/VBATT_FUSED: F401.2, Q401.2
/ARCHITECTURE/POWER/VBATT_RAW: F401.1, J401.1, J402.2, TP401.1
GND: C401.2, C402.2, C403.2, C404.1, C405.1, C501.1, C502.1, C503.2, C504.1, C505.2, C506.1, C507.1, C508.2, C509.1, C510.1, C511.1, C512.1, C601.2, C602.2, C604.2, C605.2, C606.2, C610.2, C613.2, C614.2, C615.1, C616.2, C701.2, C702.2, C703.2, C705.2, C707.2, D501.1 (K), D502.1 (K), D503.2 (A2), D602.2 (A), D604.2 (A), D606.2 (A), H401.1, H402.1, H403.1, H404.1, J401.2, J402.1, J501.5 (GND), J501.7 (GND), J502.A1 (GND), J502.A12 (GND), J502.B1 (GND), J502.B12 (GND), J502.S1 (SHIELD), J601.2 (Ext), J602.2 (Ext), J603.2 (Ext), R401.2, R508.2, R509.1, R510.1, R611.1, R613.1, R624.1, R706.1, SW501.1, TP404.1, TP601.2, TP602.2, TP603.2, TP604.2, U401.2 (GND), U501.14 (VSSA), U501.16 (VSS), U501.32 (VSS), U502.2 (GND), U601.4 (V-), U602.4 (V-), U603.4 (V-), U604.4 (V-), U605.4 (V-), U701.4 (V-), U702.4 (V-)
unnamed: D501.2 (A), R501.1
unnamed: D502.2 (A), R502.1
unnamed: J501.6 (JCLK/SWCLK), R503.1
unnamed: J501.8 (JTDO/SWO), R506.1
unnamed: J501.4 (JTMS/SWDIO), R504.1
unnamed: J501.12 (~RST), R505.1
unnamed: R508.1, U501.31 (PB8)
unnamed: R623.1, R624.2, U601.5 (+)
VBATT: C402.1, C403.1, D401.1 (K), JP401.1 (A), Q401.3, R402.2, TP402.1
VIN_SEL: C401.1, C404.2, JP401.2 (C), U401.1 (IN), U401.3 (EN)
VREF_ECG: C612.1, C613.1, C615.2, R621.2, U601.6 (-), U601.7, U604.3 (+), U605.3 (+)
VUSB: C505.1, C508.1, D503.1 (A1), F501.2, JP401.3 (B), TP501.1

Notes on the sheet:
MOUNTING
IC POWER AND DECOUPLING
MARKINGS
0.60V
0.61V
3RD ORDER SK BWORTH LPF
DC SERVO
0.59V
0.65V
0.54V
GAIN STAGE
2ND ORDER SK BWORTH LPF
1.0V
4TH ORDER UNITY SK BWORTH RECONSTRUCTION FILTER
2ND ORDER NON-UNITY SK BWORTH LPF
0.61V
DIFFERENTIAL OUTPUT DRIVER
HMI
ECG ANALOGUE REFERENCE VOLTAGE
DESIGN NOTE: 10V zener for gate oxide protection if needed.
DESIGN NOTE: Non-inverting integrator used to integrate ECG_FILT over a large time constant to return an error signal SERVO_OUT fed into the gain stage U605A, ensuring EGC_OUT is biased to VREF_EGC for maximum headroom.
LAYOUT NOTE: As close to uC pins, small C first
ECG FILTERING AND GAIN
DESIGN NOTE: 2nd order unity-gain Sallen-Key LPF with Butterworth response, Q ≈ 0.707, f_{c} ≈ 40 Hz
DESIGN NOTE: Input buffered due to unknown source impedance.
MOUNTING AND MARKINGS
DESIGN NOTE: LM358LVIDR can supply up to 40mA, for the differential driver this should be enough to provide 4 Vpp to the 100R shaker load.
SUPPLY SELECT
DESIGN NOTE: The 0.61V VREF is generated to bias the output for headroom.
JTAG INTERCONNECT
LOW DROPOUT REGULATOR
DESIGN NOTE: Typical I_{DD} current consumption: 18.0mA @ F_{HCLK} = 80MHz @ 85C 24.0mA @ F_{HCLK} = 120MHz @ 85C 33.0mA @ F_{HCLK} = 170MHz @ 85C
DESIGN NOTE: Optional 100R load direct on board.
SHAKER
Description
DESIGN NOTE: Non-stocked part, cost $0.517, used as as stocked LDO has too high a V_{dropout}
DESIGN NOTE: Non-stocked part, cost $0.583, used as simple input overcurrent protection.
DESIGN NOTE: Non-inverting gain stage, A_{v} ≈ 3 for FS use of ADC.
DESIGN NOTE: Diodes and series resistor to clamp to +3V0 and GND for protection. Typical for all analogue inputs.
CHEST EXPANSION FILTERING AND GAIN

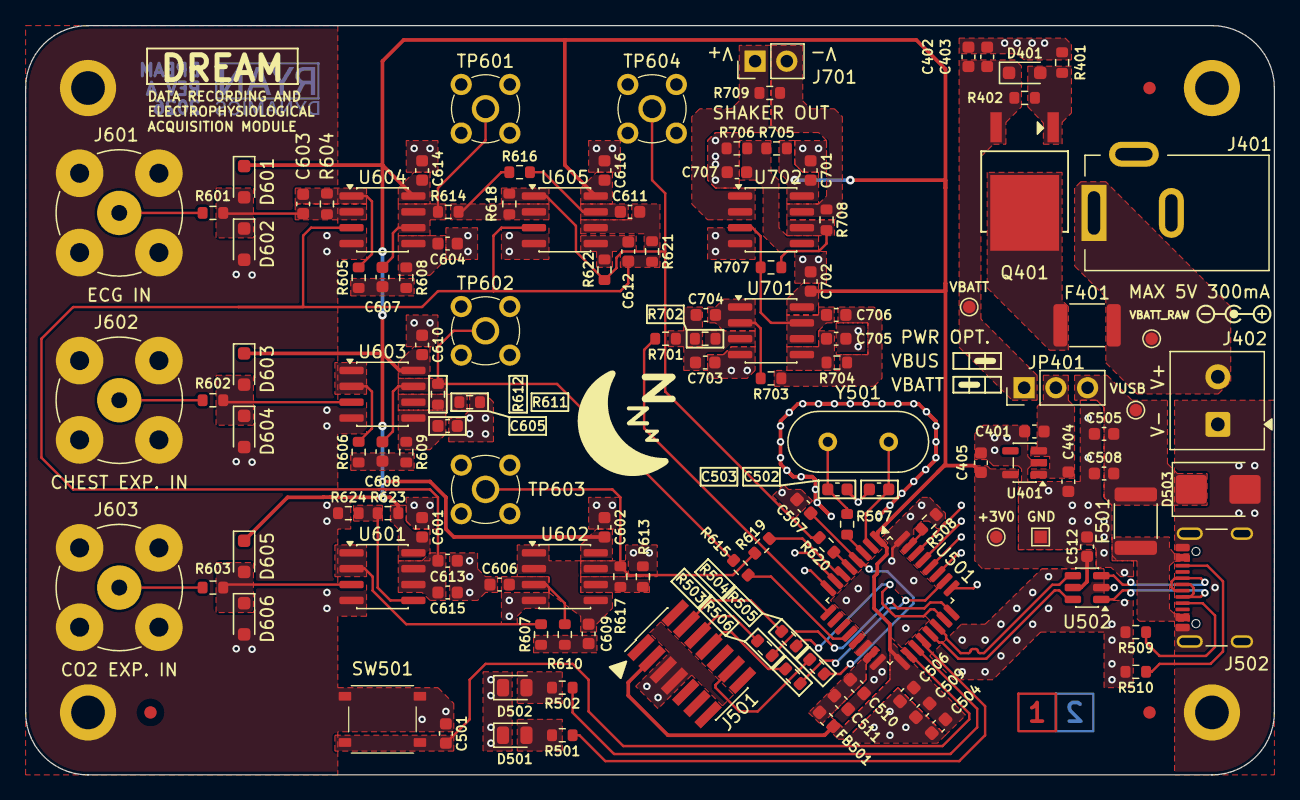
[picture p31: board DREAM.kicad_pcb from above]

Board: 2 copper layers, 100.0 x 60.0 mm, 137 parts (0 on the bottom side), 75 nets.

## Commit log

2026-04-12 feat: schematic capture and preliminary PCB layout
    [Analogue-Inputs.kicad_sch, Analogue-Outputs.kicad_sch, Block Diagram.kicad_sch, DREAM.kicad_pcb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]
2026-04-12 Update Outputs
    [DREAM-(L1-L2)_NPTH_drill_table.csv, DREAM-(L1-L2)_drill_table.csv, DREAM-B_Mask.gbr, DREAM-B_Paste.gbr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]
2026-04-14 feat: checked REV A
    [Analogue-Inputs.kicad_sch, Analogue-Outputs.kicad_sch, Block Diagram.kicad_sch, DREAM.kicad_pcb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]
2026-04-14 fix: schem and fab document
    [DREAM.kicad_pcb]
2026-04-14 fix: schematic note wording
    [Analogue-Inputs.kicad_sch, Analogue-Outputs.kicad_sch]
2026-04-14 Update Outputs (release)
    [DREAM-B_Mask.gbr, DREAM-B_Paste.gbr, DREAM-B_Silkscreen.gbr, DREAM-Edge_Cuts.gbr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]
2026-04-14 fix: ground under XTAL, untent vias, production files
    [DREAM.kicad_pcb, bom.csv, designators.csv, positions.csv]
2026-04-14 fix: net naming, NC STM32 pins, silkscreen, pin 1 indicator
    [DREAM.kicad_pcb, Microcontroller.kicad_sch, Power.kicad_sch]
2026-04-14 fix: improved crystal oscillator layout
    [DREAM.kicad_pcb, Revision History.kicad_sch]
2026-04-14 fix: add ground pour under uC
    [DREAM.kicad_pcb, Revision History.kicad_sch, positions.csv]
2026-05-09 fix: circuit schem as one sheet
    [Analogue-Inputs.kicad_sch, Analogue-Outputs.kicad_sch, Block Diagram.kicad_sch, DREAM.kicad_pcb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]
2026-05-09 feat: board image
    [DREAM.kicad_pcb]
2026-05-09 fix: erc
    [Project Architecture.kicad_sch]
